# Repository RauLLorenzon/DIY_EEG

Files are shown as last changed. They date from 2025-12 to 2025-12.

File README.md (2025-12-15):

# ADS1299_BasicEEG
Basic 8 Channel EEG PCB, Using the ADS1299 and bipolar power supply, made as a personal project
3D_model_f
3D_model_b
schematics_main
schematics_power
schematics_input
pcb_f
pcb_b

# License
CERN-OHL-P-2.0

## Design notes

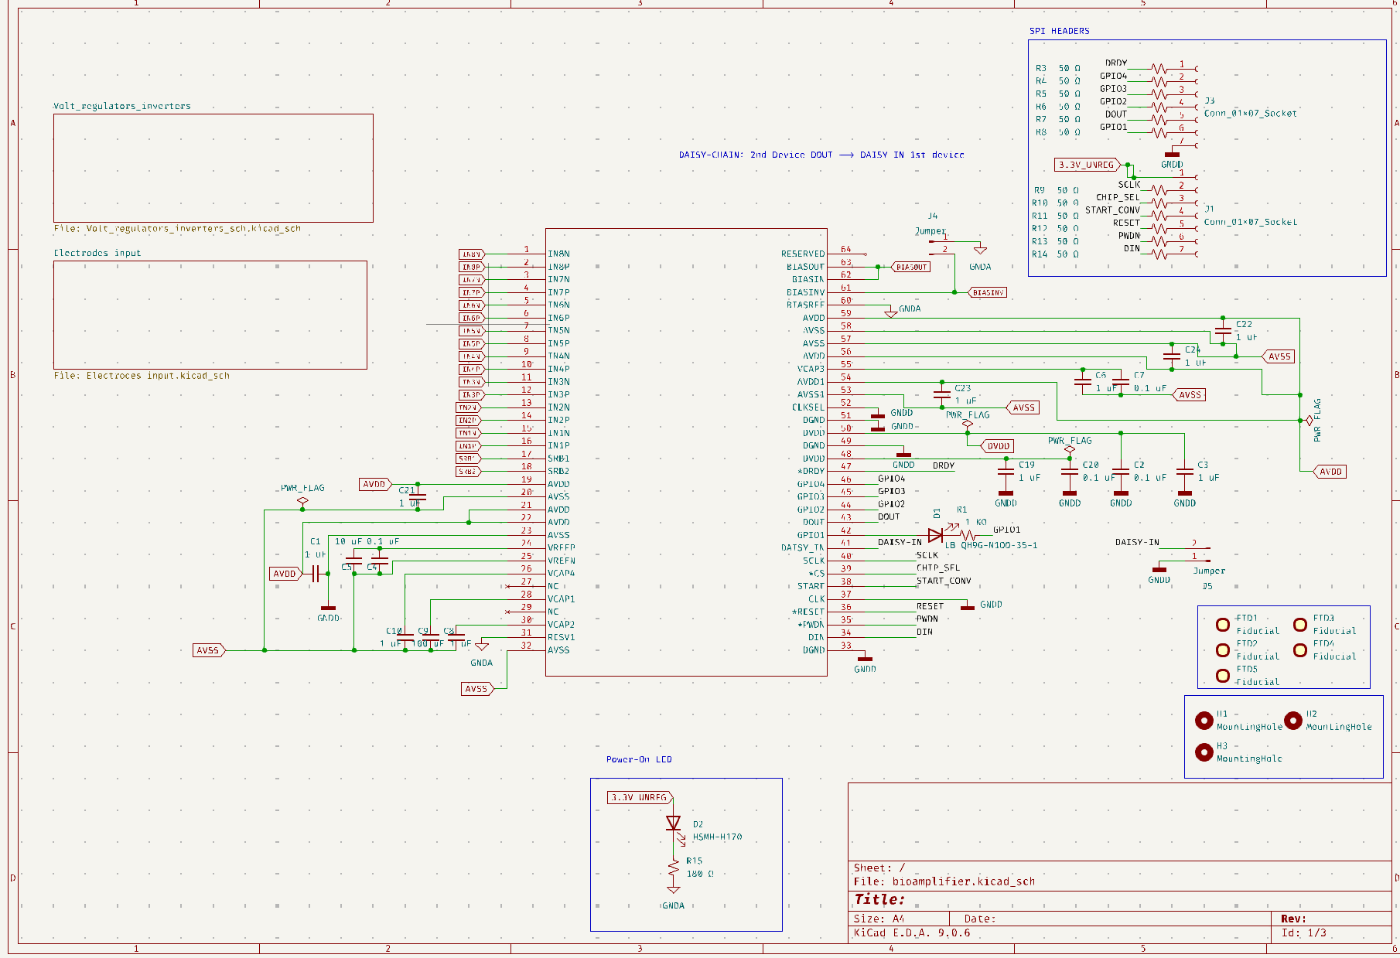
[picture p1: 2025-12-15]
References/schematics_main.png

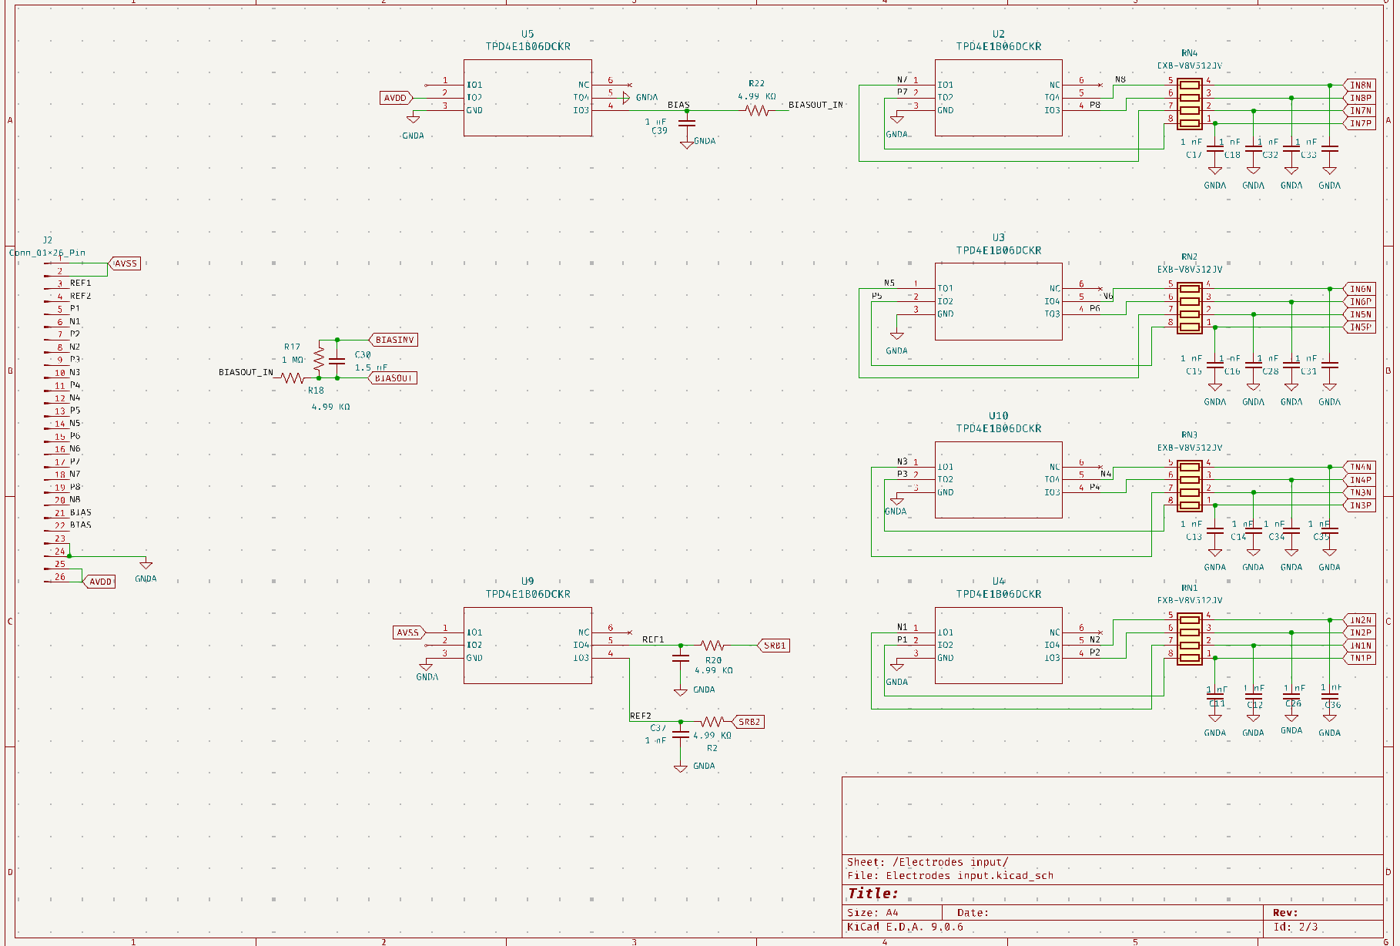
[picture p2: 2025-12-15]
References/schematics_input.png

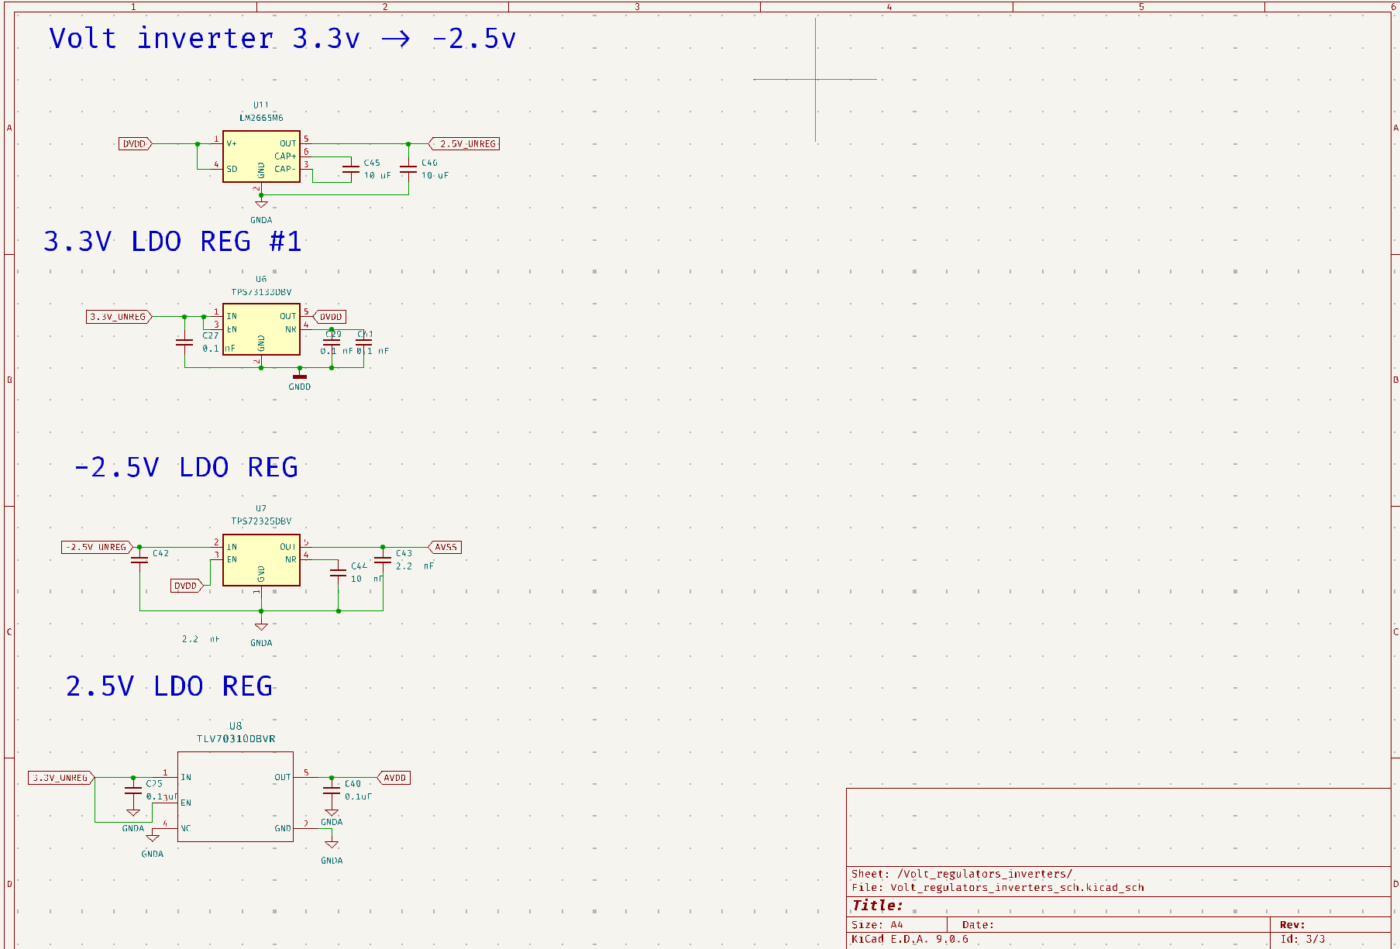
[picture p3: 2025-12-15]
References/schematics_power.png

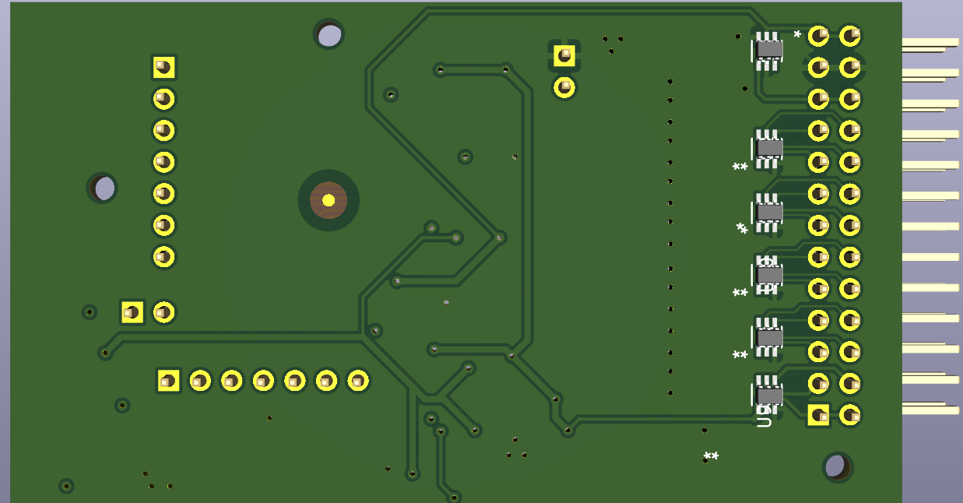
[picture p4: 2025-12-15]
References/3D_model_b.png

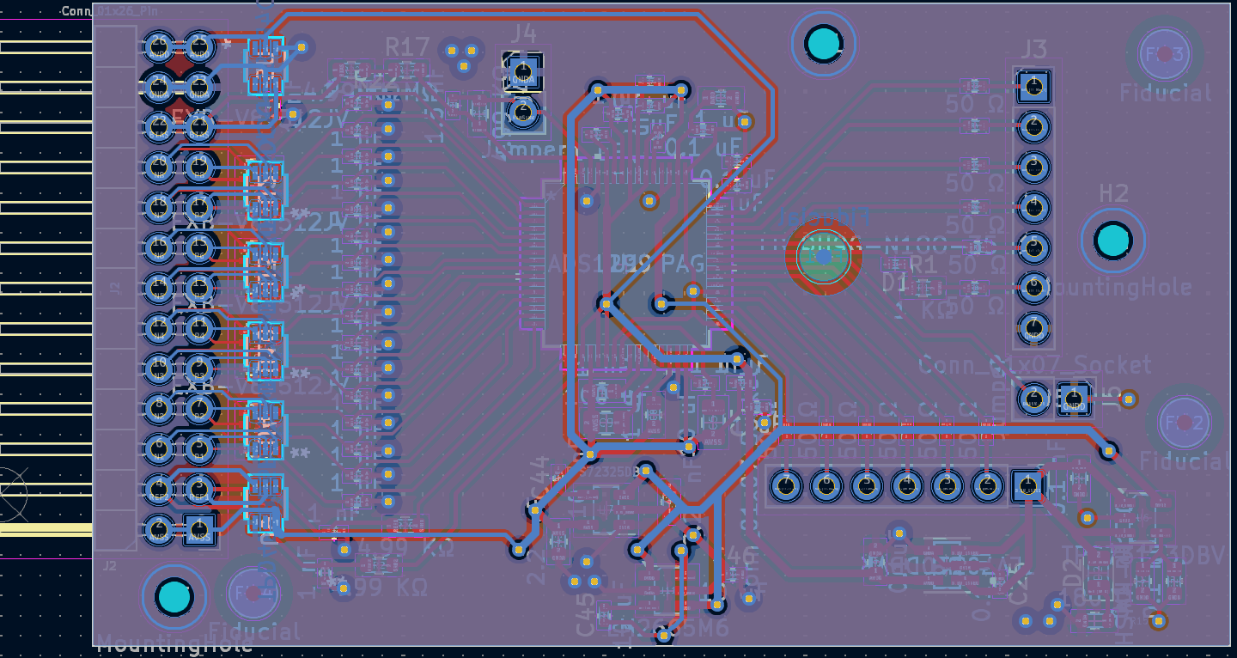
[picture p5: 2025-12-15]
References/pcb_b.png

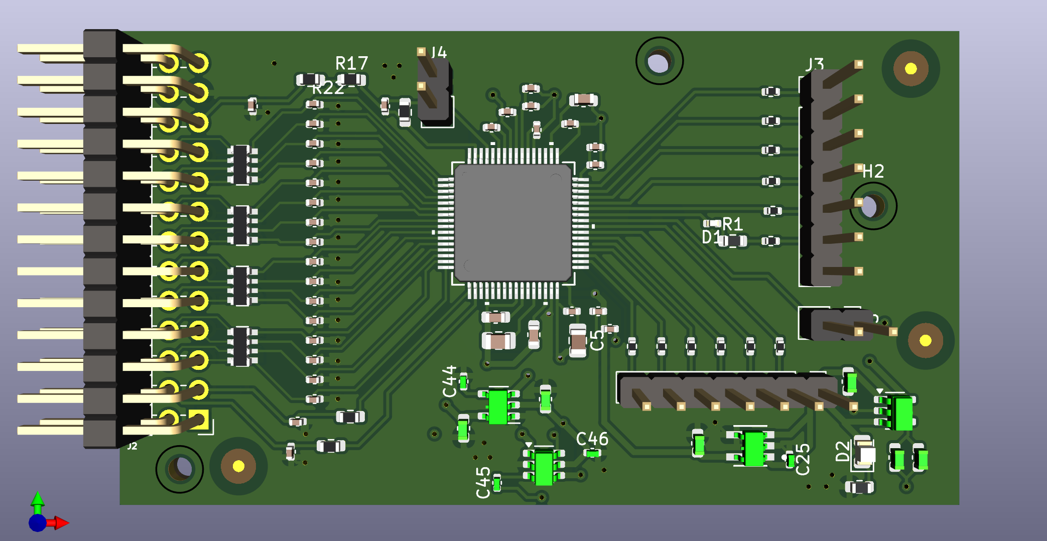
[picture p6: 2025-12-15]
References/3D_model_f.png

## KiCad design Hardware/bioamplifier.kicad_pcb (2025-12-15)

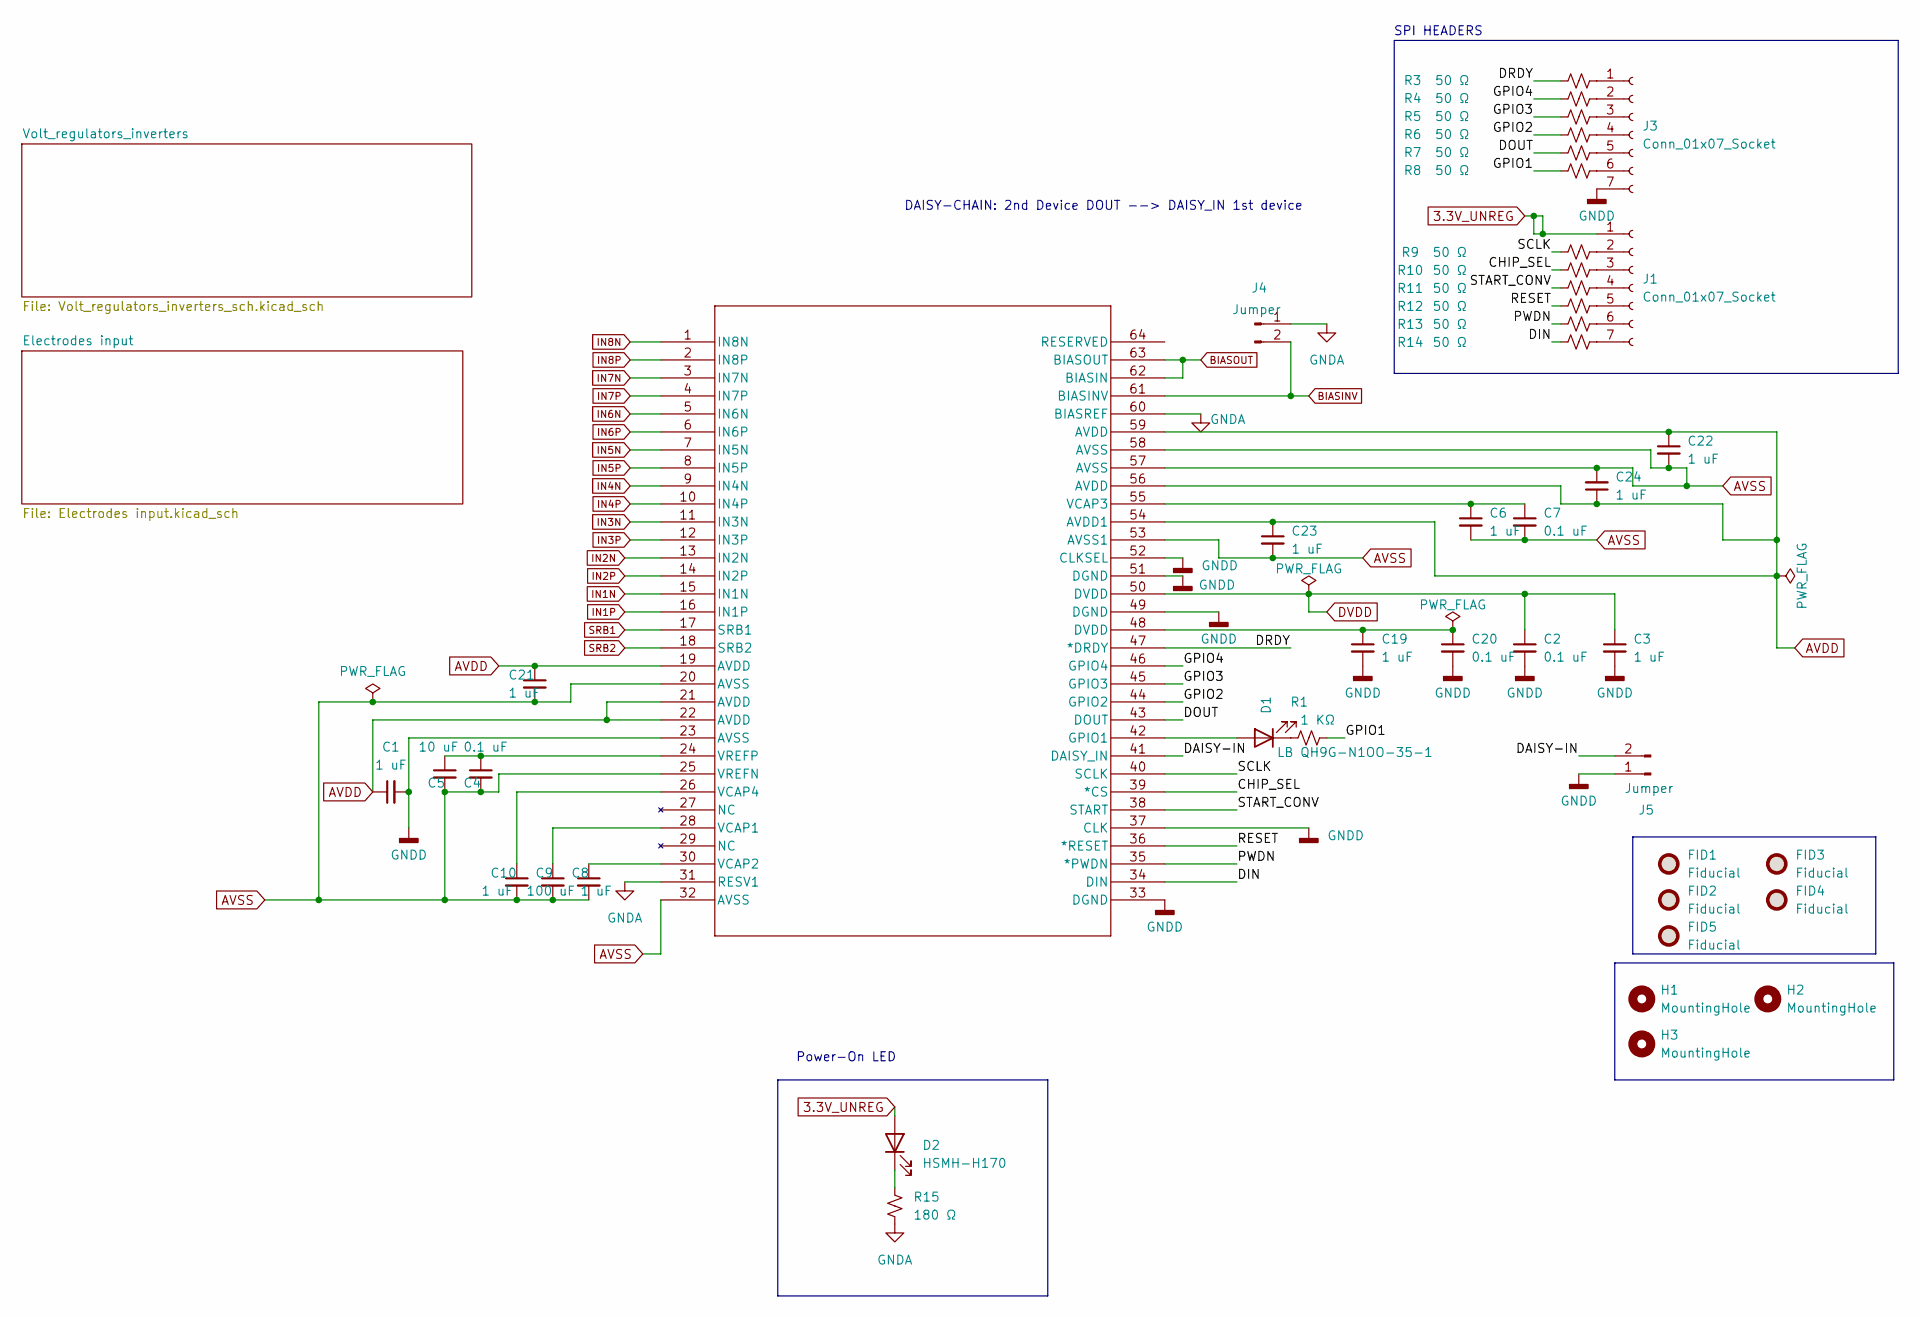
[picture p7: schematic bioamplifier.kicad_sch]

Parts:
C1, C6, C19, C21, C22, C23, C24: 1 uF; C_0402_1005Metric
C2, C4, C7, C20: 0.1 uF; C_0402_1005Metric
C3, C8, C10: 1 uF; C_0603_1608Metric
C5: 10 uF; C_0805_2012Metric
C9: 100 uF; C_0805_2012Metric
D1: LB QH9G-N1OO-35-1; LED_0402_1005Metric
D2: HSMH-H170; LED_0805_2012Metric; MPN HSMH-H170; Mouser Price/Stock 0,474
FID1, FID2, FID3, FID4, FID5: Fiducial; Fiducial_1mm_Mask3mm
H1, H2, H3: MountingHole; MountingHole_2mm
J1, J3: Conn_01x07_Socket; PinHeader_1x07_P2.54mm_Vertical
J4, J5: Jumper; PinHeader_1x02_P2.54mm_Vertical
R1: 1 KΩ; R_0603_1608Metric
R3, R4, R5, R6, R7, R8, R9, R10, R11, R12, R13, R14: 50 Ω; R_0402_1005Metric
R15: 180 Ω; R_0603_1608Metric
U1: ADS1299IPAG; PAG64_TEX

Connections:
3.3V_UNREG: D2.2 (A), J1.1; also elsewhere on the board
/CHIP_SEL: R10.1, U1.39 (*CS)
/DAISY-IN: J5.2, U1.41 (DAISY_IN)
/DIN: R14.1, U1.34 (DIN)
/DOUT: R7.1, U1.43 (DOUT)
/DRDY: R3.1, U1.47 (*DRDY)
/GPIO1: R1.2, R8.1
/GPIO2: R6.1, U1.44 (GPIO2)
/GPIO3: R5.1, U1.45 (GPIO3)
/GPIO4: R4.1, U1.46 (GPIO4)
/PWDN: R13.1, U1.35 (*PWDN)
/RESET: R12.1, U1.36 (*RESET)
/SCLK: R9.1, U1.40 (SCLK)
/START_CONV: R11.1, U1.38 (START)
AVDD: C1.1, C21.1, C22.1, C23.1, C24.1, U1.19 (AVDD), U1.21 (AVDD), U1.22 (AVDD), U1.54 (AVDD1), U1.56 (AVDD), U1.59 (AVDD); also elsewhere on the board
AVSS: C4.2, C5.2, C6.2, C7.2, C8.2, C9.2, C10.2, C21.2, C22.2, C23.2, C24.2, U1.20 (AVSS), U1.25 (VREFN), U1.32 (AVSS), U1.53 (AVSS1), U1.57 (AVSS), U1.58 (AVSS); also elsewhere on the board
BIASINV: J4.2, U1.61 (BIASINV); also elsewhere on the board
BIASOUT: U1.62 (BIASIN), U1.63 (BIASOUT); also elsewhere on the board
DVDD: C2.1, C3.1, U1.50 (DVDD); also elsewhere on the board
GNDA: J4.1, R15.2, U1.31 (RESV1), U1.60 (BIASREF); also elsewhere on the board
GNDD: C1.2, C2.2, C3.2, C19.2, C20.2, J3.7, J5.1, U1.23 (AVSS), U1.33 (DGND), U1.37 (CLK), U1.49 (DGND), U1.51 (DGND), U1.52 (CLKSEL); also elsewhere on the board
IN1N: U1.15 (IN1N); also elsewhere on the board
IN1P: U1.16 (IN1P); also elsewhere on the board
IN2N: U1.13 (IN2N); also elsewhere on the board
IN2P: U1.14 (IN2P); also elsewhere on the board
IN3N: U1.11 (IN3N); also elsewhere on the board
IN3P: U1.12 (IN3P); also elsewhere on the board
IN4N: U1.9 (IN4N); also elsewhere on the board
IN4P: U1.10 (IN4P); also elsewhere on the board
IN5N: U1.7 (IN5N); also elsewhere on the board
IN5P: U1.8 (IN5P); also elsewhere on the board
IN6N: U1.5 (IN6N); also elsewhere on the board
IN6P: U1.6 (IN6P); also elsewhere on the board
IN7N: U1.3 (IN7N); also elsewhere on the board
IN7P: U1.4 (IN7P); also elsewhere on the board
IN8N: U1.1 (IN8N); also elsewhere on the board
IN8P: U1.2 (IN8P); also elsewhere on the board
unnamed: C19.1, C20.1, U1.48 (DVDD)
unnamed: D1.2 (A), U1.42 (GPIO1)
unnamed: D1.1 (K), R1.1
unnamed: D2.1 (K), R15.1
unnamed: J1.2, R9.2
unnamed: J1.3, R10.2
unnamed: J1.4, R11.2
unnamed: J1.5, R12.2
unnamed: J1.6, R13.2
unnamed: J1.7, R14.2
unnamed: J3.1, R3.2
unnamed: J3.2, R4.2
unnamed: J3.3, R5.2
unnamed: J3.4, R6.2
unnamed: J3.5, R7.2
unnamed: J3.6, R8.2
unnamed: C9.1, U1.28 (VCAP1)
unnamed: C8.1, U1.30 (VCAP2)
unnamed: C6.1, C7.1, U1.55 (VCAP3)
unnamed: C10.1, U1.26 (VCAP4)
unnamed: C4.1, C5.1, U1.24 (VREFP)
SRB1: U1.17 (SRB1); also elsewhere on the board
SRB2: U1.18 (SRB2); also elsewhere on the board

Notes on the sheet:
Power-On LED
DAISY-CHAIN: 2nd Device DOUT --> DAISY_IN 1st device
SPI HEADERS

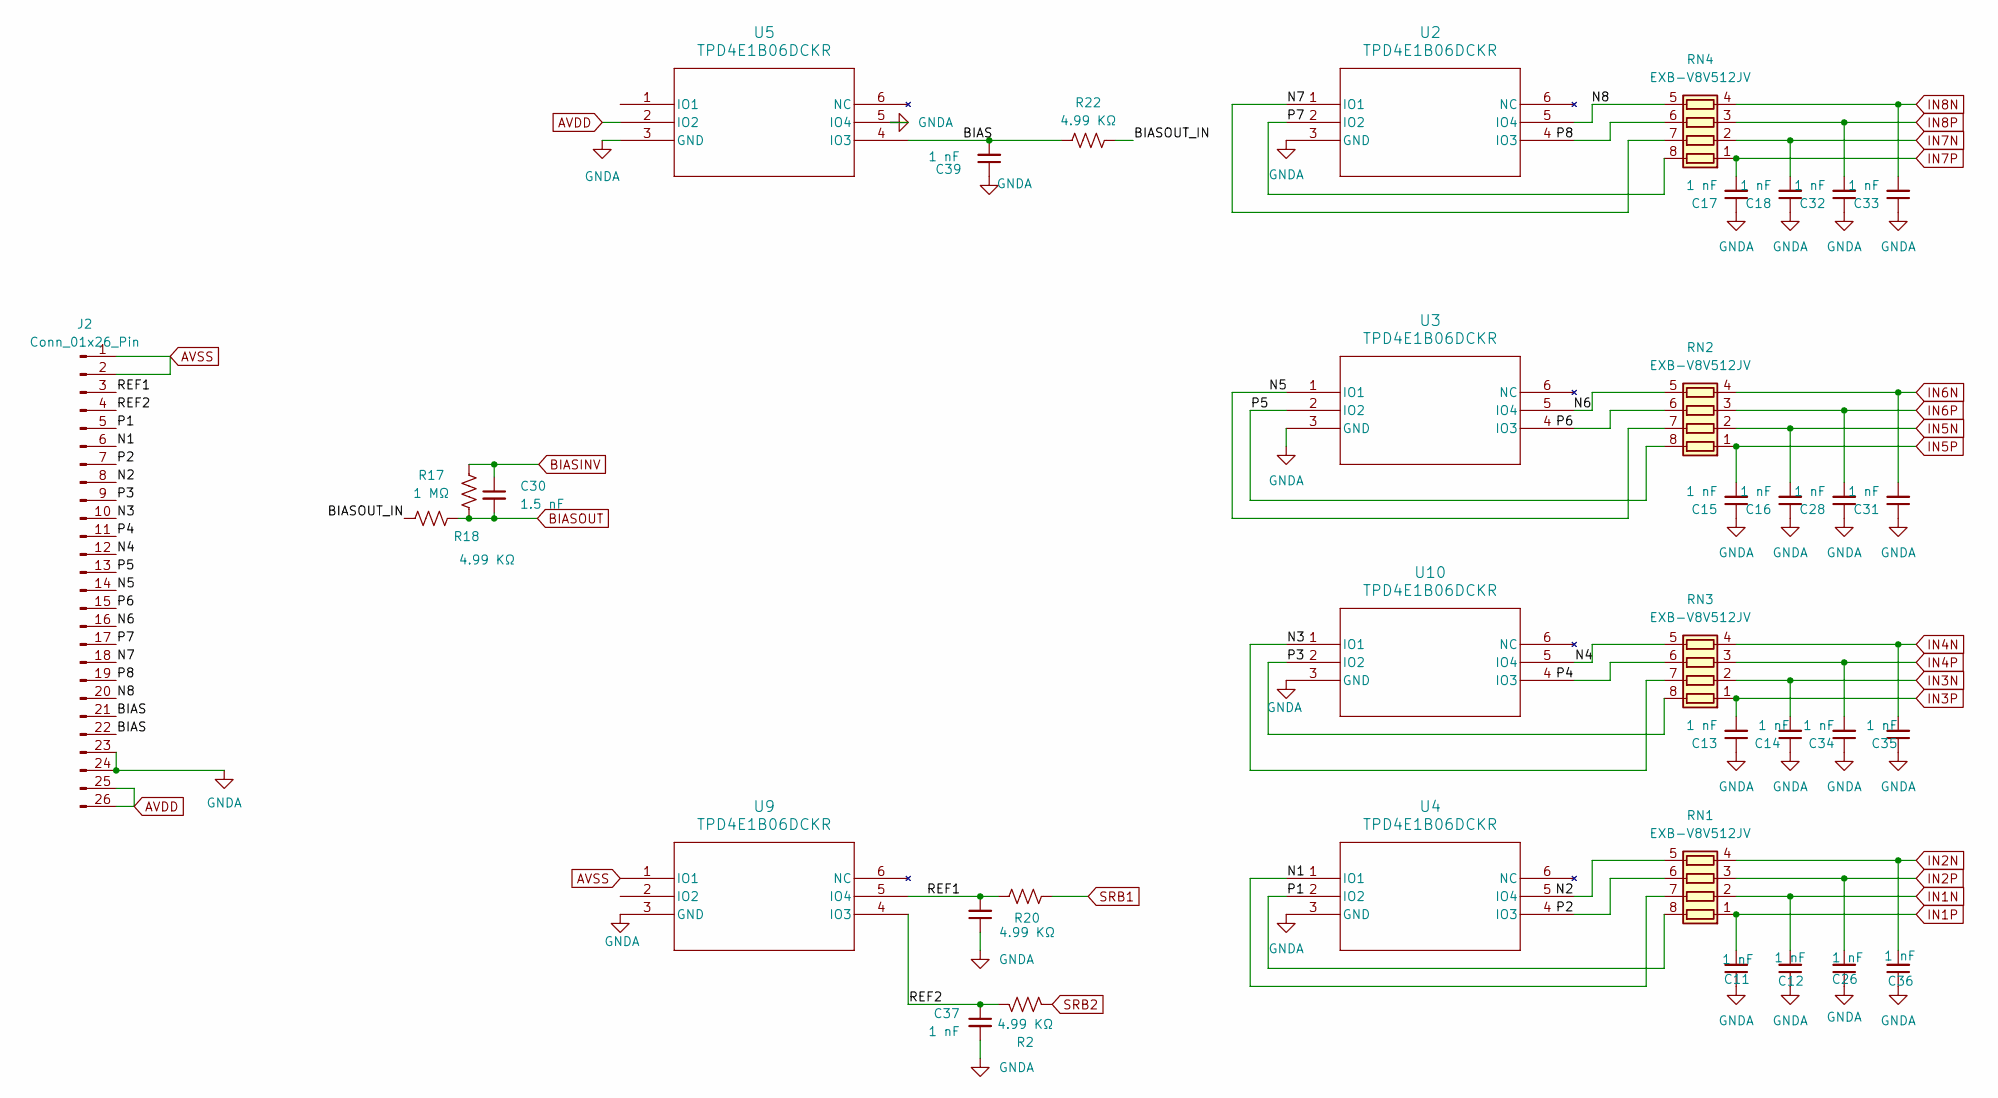
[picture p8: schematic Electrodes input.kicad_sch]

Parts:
C11, C12, C13, C14, C15, C16, C17, C18, C26, C28, C31, C32, C33, C34, C35, C36, C37, C38, C39: 1 nF; C_0402_1005Metric
C30: 1.5 nF; C_0402_1005Metric
J2: Conn_01x26_Pin; PinHeader_2x13_P2.54mm_Horizontal
R2, R18, R20, R22: 4.99 KΩ; R_0603_1608Metric
R17: 1 MΩ; R_0603_1608Metric
RN1, RN2, RN3, RN4: EXB-V8V512JV; R_Array_Convex_4x0603
U2, U3, U4, U5, U9, U10: TPD4E1B06DCKR; DCK6_TEX

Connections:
/Electrodes input/BIAS: C39.2, J2.21, J2.22, R22.1, U5.4 (IO3)
/Electrodes input/BIASOUT_IN: R17.1, R22.2
/Electrodes input/N1: J2.6, RN1.7 (R2.2), U4.1 (IO1)
/Electrodes input/N2: J2.8, RN1.5 (R4.2), U4.5 (IO4)
/Electrodes input/N3: J2.10, RN3.7 (R2.2), U10.1 (IO1)
/Electrodes input/N4: J2.12, RN3.5 (R4.2), U10.5 (IO4)
/Electrodes input/N5: J2.14, RN2.7 (R2.2), U3.1 (IO1)
/Electrodes input/N6: J2.16, RN2.5 (R4.2), U3.5 (IO4)
/Electrodes input/N7: J2.18, RN4.7 (R2.2), U2.1 (IO1)
/Electrodes input/N8: J2.20, RN4.5 (R4.2), U2.5 (IO4)
/Electrodes input/P1: J2.5, RN1.8 (R1.2), U4.2 (IO2)
/Electrodes input/P2: J2.7, RN1.6 (R3.2), U4.4 (IO3)
/Electrodes input/P3: J2.9, RN3.8 (R1.2), U10.2 (IO2)
/Electrodes input/P4: J2.11, RN3.6 (R3.2), U10.4 (IO3)
/Electrodes input/P5: J2.13, RN2.8 (R1.2), U3.2 (IO2)
/Electrodes input/P6: J2.15, RN2.6 (R3.2), U3.4 (IO3)
/Electrodes input/P7: J2.17, RN4.8 (R1.2), U2.2 (IO2)
/Electrodes input/P8: J2.19, RN4.6 (R3.2), U2.4 (IO3)
/Electrodes input/REF1: C38.2, J2.3, R20.1, U9.5 (IO4)
/Electrodes input/REF2: C37.1, J2.4, R2.1, U9.4 (IO3)
AVDD: J2.25, J2.26, U5.2 (IO2); also elsewhere on the board
AVSS: J2.1, J2.2, U9.1 (IO1); also elsewhere on the board
BIASINV: C30.1, R18.2; also elsewhere on the board
BIASOUT: C30.2, R17.2, R18.1; also elsewhere on the board
GNDA: C11.1, C12.1, C13.1, C14.1, C15.1, C16.1, C17.1, C18.1, C26.1, C28.1, C31.1, C32.1, C33.1, C34.1, C35.1, C36.1, C37.2, C38.1, C39.1, J2.23, J2.24, U2.3 (GND), U3.3 (GND), U4.3 (GND), U5.3 (GND), U5.5 (IO4), U9.3 (GND), U10.3 (GND); also elsewhere on the board
IN1N: C12.2, RN1.2 (R2.1); also elsewhere on the board
IN1P: C11.2, RN1.1 (R1.1); also elsewhere on the board
IN2N: C36.2, RN1.4 (R4.1); also elsewhere on the board
IN2P: C26.2, RN1.3 (R3.1); also elsewhere on the board
IN3N: C14.2, RN3.2 (R2.1); also elsewhere on the board
IN3P: C13.2, RN3.1 (R1.1); also elsewhere on the board
IN4N: C35.2, RN3.4 (R4.1); also elsewhere on the board
IN4P: C34.2, RN3.3 (R3.1); also elsewhere on the board
IN5N: C16.2, RN2.2 (R2.1); also elsewhere on the board
IN5P: C15.2, RN2.1 (R1.1); also elsewhere on the board
IN6N: C31.2, RN2.4 (R4.1); also elsewhere on the board
IN6P: C28.2, RN2.3 (R3.1); also elsewhere on the board
IN7N: C18.2, RN4.2 (R2.1); also elsewhere on the board
IN7P: C17.2, RN4.1 (R1.1); also elsewhere on the board
IN8N: C33.2, RN4.4 (R4.1); also elsewhere on the board
IN8P: C32.2, RN4.3 (R3.1); also elsewhere on the board
SRB1: R20.2; also elsewhere on the board
SRB2: R2.2; also elsewhere on the board

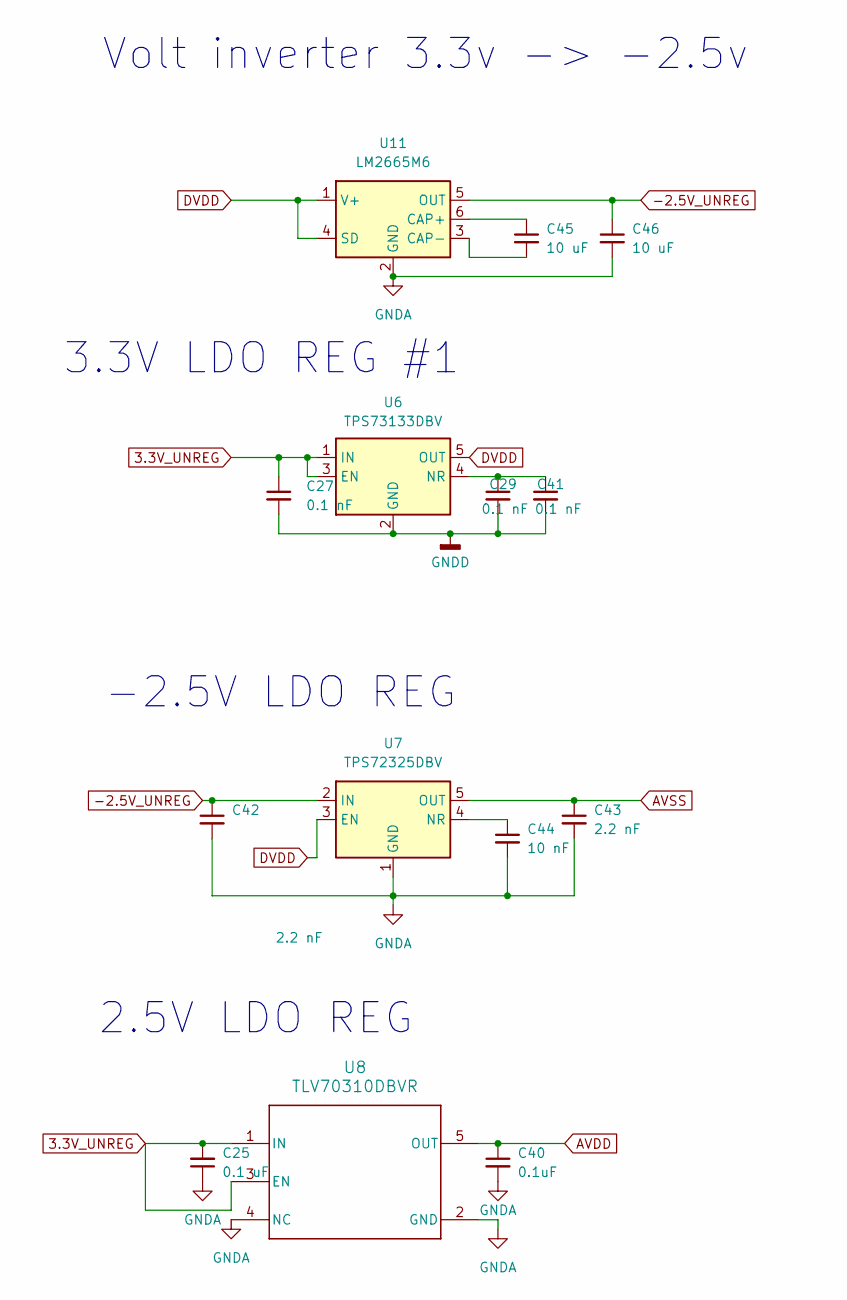
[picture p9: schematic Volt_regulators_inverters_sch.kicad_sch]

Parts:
C25: 0.1 uF; C_0402_1005Metric
C27, C29, C41: 0.1 nF; C_0603_1608Metric
C40: 0.1uF; C_0603_1608Metric
C42, C43: 2.2 nF; C_0603_1608Metric
C44: 10 nF; C_0402_1005Metric
C45, C46: 10 uF; C_0402_1005Metric
U6: TPS73133DBV; SOT-23-5
U7: TPS72325DBV; SOT-23-5
U8: TLV70310DBVR; DBV0005A-IPC_A
U11: LM2665M6; SOT-23-6

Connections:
3.3V_UNREG: C25.2, C27.1, U6.1 (IN), U6.3 (EN), U8.1 (IN), U8.3 (EN); also elsewhere on the board
-2.5V_UNREG: C42.1, C46.1, U7.2 (IN), U11.5 (OUT)
AVDD: C40.1, U8.5 (OUT); also elsewhere on the board
AVSS: C43.1, U7.5 (OUT); also elsewhere on the board
DVDD: U6.5 (OUT), U7.3 (EN), U11.1 (V+), U11.4 (SD); also elsewhere on the board
GNDA: C25.1, C40.2, C42.2, C43.2, C44.2, C46.2, U7.1 (GND), U8.2 (GND), U8.4 (NC), U11.2 (GND); also elsewhere on the board
GNDD: C27.2, C29.2, C41.2, U6.2 (GND); also elsewhere on the board
unnamed: C29.1, C41.1, U6.4 (NR)
unnamed: C44.1, U7.4 (NR)
unnamed: C45.1, U11.6 (CAP+)
unnamed: C45.2, U11.3 (CAP-)

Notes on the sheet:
Volt inverter 3.3v -> -2.5v
3.3V LDO REG #1
-2.5V LDO REG
2.5V LDO REG

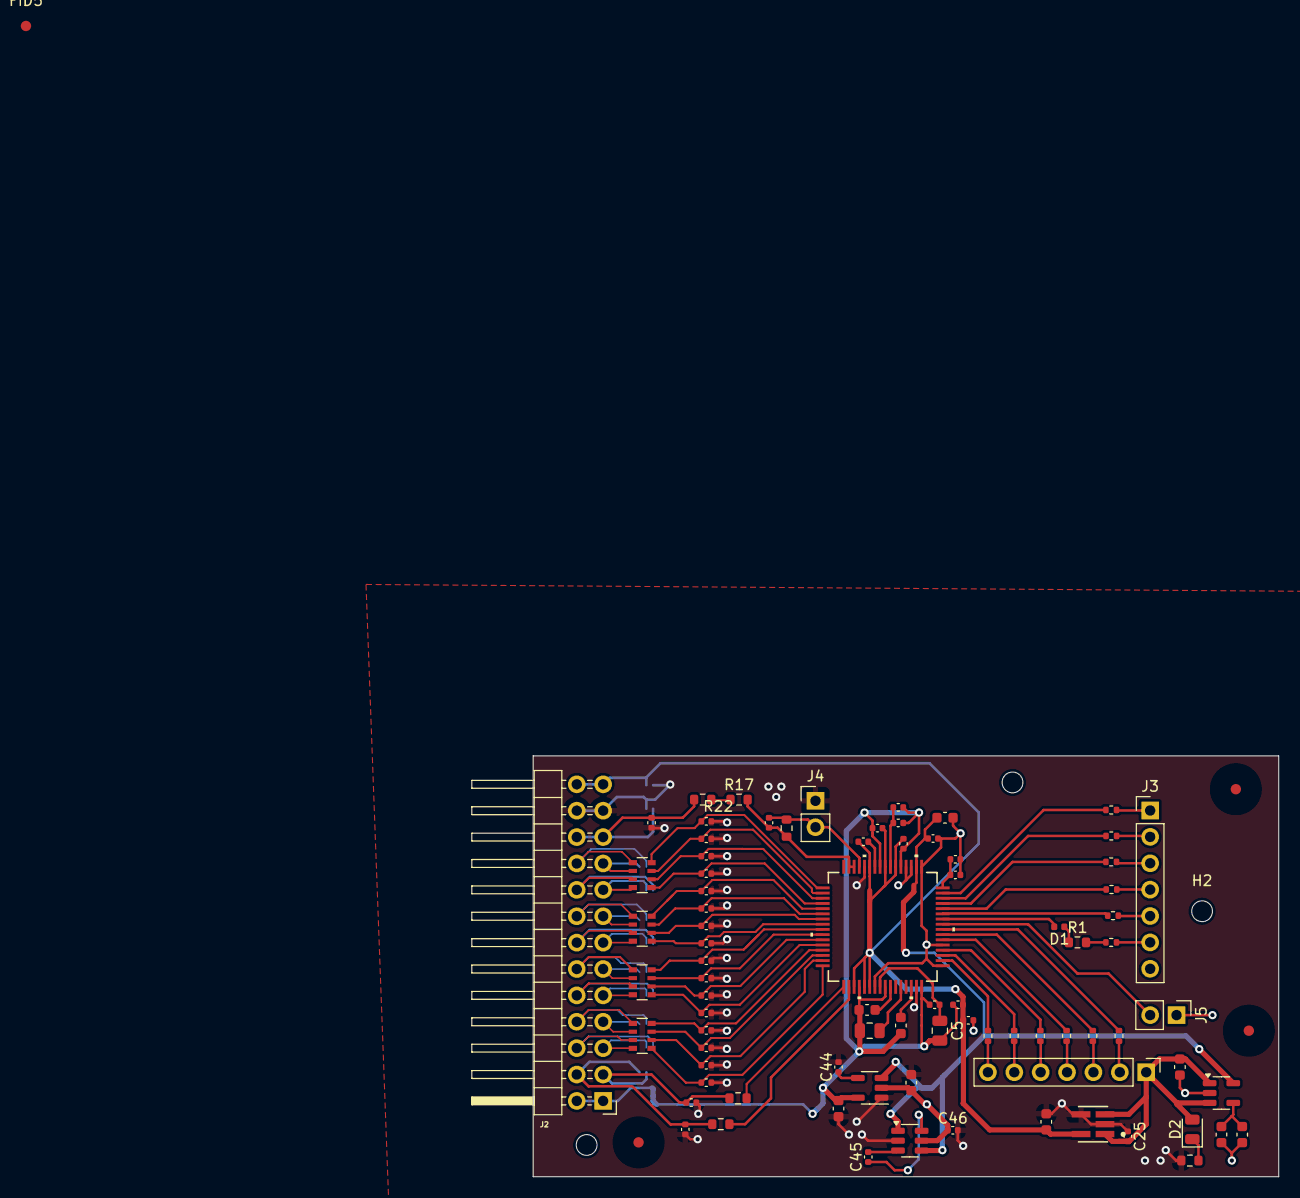
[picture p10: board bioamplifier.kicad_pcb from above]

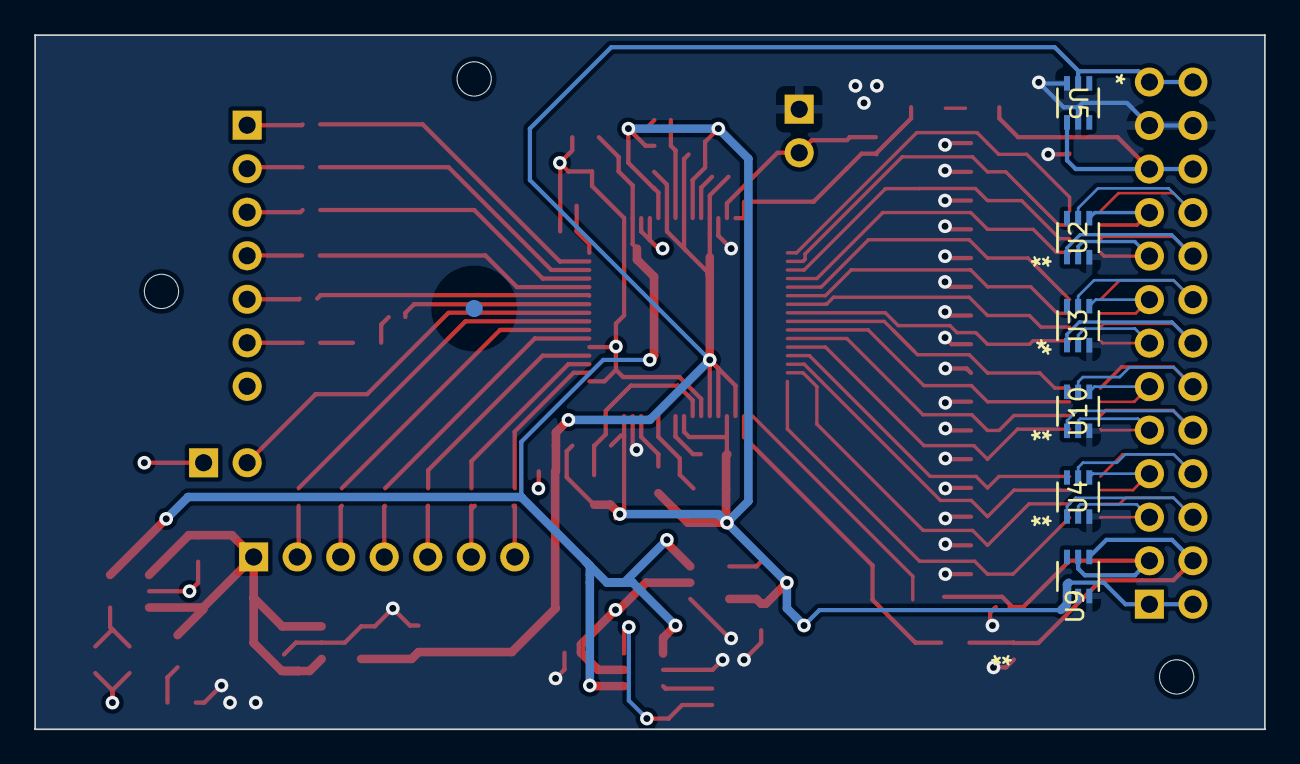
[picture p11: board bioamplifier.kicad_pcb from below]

Board: 4 copper layers, 71.8 x 40.5 mm, 95 parts (7 on the bottom side), 85 nets.

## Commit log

2024-03-25 Add files via upload
    Basic Schematic done, Start of PCB design
    [Electrodes input.kicad_sch, bioamplifier.kicad_pcb, bioamplifier.kicad_sch]
2024-09-13 DIY_EEG board design changes
    [Electrodes input.kicad_sch, freerouting.dsn]
2024-09-13 design changes
    [Electrodes input.kicad_sch, bioamplifier.kicad_pcb, bioamplifier.kicad_sch]
2024-09-23 redone analog inputs, passive component footprints now match real components, added library for possible 4 element capacitor array
    [Electrodes input.kicad_sch, bioamplifier.kicad_pcb, bioamplifier.kicad_sch]
2024-10-07 redone analog inputs, decoupling caps
    [Electrodes input.kicad_sch, bioamplifier.kicad_pcb, bioamplifier.kicad_sch]
2024-10-08 added symbol/ footprint libraris for a bipolar supply design change
    [bioamplifier.kicad_pcb]
2024-10-23 added schematics components for a bipolar power supply
    [Volt_regulators_inverters_sch.kicad_sch, bioamplifier.kicad_sch]
2024-12-10 schematics redone, TODO: Pcb component placement
    [Volt_regulators_inverters_sch.kicad_sch, bioamplifier.kicad_pcb, bioamplifier.kicad_sch]
2024-12-18 changes to pcb and schematics
    [Volt_regulators_inverters_sch.kicad_sch, bioamplifier.kicad_pcb, bioamplifier.kicad_sch]
2024-12-19 removed 5V LDO Regulator
    [Volt_regulators_inverters_sch.kicad_sch, bioamplifier.kicad_pcb, bioamplifier.kicad_sch]
2025-02-25 power pin layout change
    [Volt_regulators_inverters_sch.kicad_sch, bioamplifier.kicad_pcb, bioamplifier.kicad_sch]
2025-05-27 Fix Last DRC Errors
    [Electrodes input.kicad_sch, Volt_regulators_inverters_sch.kicad_sch, bioamplifier.kicad_pcb, bioamplifier.kicad_sch]
2025-05-27 Fix Label Error
    [Electrodes input.kicad_sch, bioamplifier.kicad_pcb]
2025-05-29 Fix Grounding
    [bioamplifier.kicad_pcb]
2025-06-15 Add Fiducials, Mounting holes, 3d models
    [Volt_regulators_inverters_sch.kicad_sch, bioamplifier.kicad_pcb, bioamplifier.kicad_sch]
2025-06-23 Remove redundant components
    [Electrodes input.kicad_sch, Volt_regulators_inverters_sch.kicad_sch, bioamplifier-B_Cu.gbr, bioamplifier-B_Fab.gbr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]
2025-06-23 Add Daisychain jumper
    [Electrodes input.kicad_sch, bioamplifier.kicad_pcb, bioamplifier.kicad_sch]
2025-06-23 Fix unconnected components
    [bioamplifier.kicad_pcb]
2025-06-23 Add poweron Led
    [bioamplifier.kicad_pcb, bioamplifier.kicad_sch]
2025-07-08 TODO: fix drc
    [bioamplifier.kicad_pcb]
2025-09-17 TODO: GND pours & planes separation
    [Electrodes input.kicad_sch, bioamplifier.kicad_pcb, bioamplifier.kicad_sch]
2025-10-08 Fix GndA Avss connection, standardize grids
    [Electrodes input.kicad_sch, bioamplifier.kicad_pcb, bioamplifier.kicad_sch]
2025-11-08 Flip capacitors from back
    [bioamplifier.kicad_pcb]
2025-11-11 fix DRC errors, redone GNDD
    [bioamplifier-B_Cu.gbr, bioamplifier-B_Fab.gbr, bioamplifier-B_Mask.gbr, bioamplifier-B_Paste.gbr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]
2025-11-15 Add final changes
    [Volt_regulators_inverters_sch.kicad_sch, bioamplifier.kicad_pcb, bioamplifier.kicad_sch]
2025-12-15 feat: add preview images
    [Volt_regulators_inverters_sch.kicad_sch, bioamplifier-B_Cu.gbr, bioamplifier-B_Fab.gbr, bioamplifier-B_Mask.gbr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]
